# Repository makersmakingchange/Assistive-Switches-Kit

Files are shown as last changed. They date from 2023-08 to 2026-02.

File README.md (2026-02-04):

# Assistive Switches Kit
<!--- SUMMARY  --->

The [Assistive Switches Kit](https://www.makersmakingchange.com/s/product/assistive-switches-kit/01tJR0000006998YAA) provides an assortment of assistive switches and is intended to provide some different options if you want to try some devices, or get your AT Library started.

## Assistive Switches Kit
### Summary

| Name                 | MMC Library Link | GitHub Repository |                          
|----------------------|-----------------|---------------------------------------------------------------------------------------------------------------------------------------------|
| Raindrop Switch      | https://www.makersmakingchange.com/s/product/raindrop-switch/01tJR000000693tYAA | https://github.com/makersmakingchange/Raindrop-Switch |
| Light Touch Switch   | https://www.makersmakingchange.com/s/product/light-touch-switch/01tJR00000068zTYAQ | https://github.com/makersmakingchange/Light-Touch-Switch |
| Interact Switch      | https://www.makersmakingchange.com/s/product/interact-switch/01tJR000000698vYAA | https://github.com/makersmakingchange/Interact-Switch |
| MMC60 Switch         | https://makersmakingchange.com/s/product/mmc60-switch/01tJR000000693rYAA | https://github.com/makersmakingchange/MMC60_Assistive_Switch |

### Raindrop Switch
Low force switch well-suited for use by a finger or head.

### Light Touch Switch
Low force switch well-suited for use by a finger.

### Interact Switch
Medium force switch that is activated through applying pressure on the top surface.

### MMC60 Switch
The switch is activated by applying pressure on the top surface. This switch can be connected to any standard AT interface, and can also be used with the Xbox Adaptive Controller. The kit contains different colours and textures of interchangeable button tops.

---

<!-- ABOUT MMC START -->
## About Makers Making Change
[Makers Making Change Logo](https://www.makersmakingchange.com/)

Makers Making Change is a program of [Neil Squire](https://www.neilsquire.ca/), a Canadian non-profit that uses technology, knowledge, and passion to empower people with disabilities.

Makers Making Change leverages the capacity of community based Makers, Disability Professionals and Volunteers to develop and deliver affordable Open Source Assistive Technologies.

 - Website: [www.MakersMakingChange.com](https://www.makersmakingchange.com/)
 - GitHub: [makersmakingchange](https://github.com/makersmakingchange)
 - Bluesky: [@makersmakingchange.bsky.social](https://bsky.app/profile/makersmakingchange.bsky.social)
 - Instagram: [@makersmakingchange](https://www.instagram.com/makersmakingchange)
 - Facebook: [makersmakechange](https://www.facebook.com/makersmakechange)
 - LinkedIn: [Neil Squire Society](https://www.linkedin.com/company/neil-squire-society/)
 - Thingiverse: [makersmakingchange](https://www.thingiverse.com/makersmakingchange/about)
 - Printables: [MakersMakingChange](https://www.printables.com/@MakersMakingChange)

### Contact Us
For technical questions, to get involved, or to share your experience we encourage you to [visit our website](https://www.makersmakingchange.com/) or [contact us](https://www.makersmakingchange.com/s/contact).
<!-- ABOUT MMC END -->

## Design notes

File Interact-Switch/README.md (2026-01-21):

 # Interact Switch
<!---  SUMMARY A brief summary of the project. What it does, who it is for, how much it costs. --->

The Interact Switch is an open source assistive switch. The switch is comprised of 3D printed parts and off-the-shelf electronics. The Interact Switch is a high quality, modular 3D printable switch design. The tactile feel of the switch is on par with commercial switches, coming in at about 35 gf of activation force across the surface of the switch. The base has the same footprint as a Jellybean switch, and should work with any Jellybean switch mounts.

There are a wide array of different designs: from a simple flat button, to textured designs, to a dome, and even some wobble switch variants.

The switch base incorporates 6 slots that are ideal for a variety of mounting options, including using hook and loop straps (e.g., VELCRO). The overall cost of materials is about $8 (plus $8 for component shipping).

A 3D printed Interact Switch with smiley topper

## More info at
- [Makers Making Change Library Page](https://www.makersmakingchange.com/s/product/interact-switch/01tJR000000698vYAA)

## How to Obtain the Device
### 1. Do-it-Yourself (DIY) or Do-it-Together (DIT)

This is an open-source assistive technology, so anyone is free to build it. All of the files and instructions required to build the device are contained within this repository. Refer to the Maker Guide below.

### 2. Request a build of this device

You may also submit a build request through the [MMC Library Page](https://www.makersmakingchange.com/s/product/interact-switch/01tJR000000698vYAA) to have a volunteer maker build the device. As the requestor, you are responsible for reimbursing the maker for the cost of materials and any shipping.

### 3. Build this device for someone else

If you have the skills and equipment to build this device, and would like to donate your time to create the device for someone who needs it, visit the [MMC Maker Wanted](https://makersmakingchange.com/maker-wanted/) section.

## Build Instructions

### 1. Read through the Maker Guide

The Maker Guide  [EN](/Documentation/Interact_Switch_Maker_Guide.pdf), WIP <!---([FR](/Documentation/FR_Interact_Switch_Maker_Guide.pdf)) --->  contains all the necessary information to build this device, including tool lists, assembly instructions, programming instructions (if applicable) and testing.

### 2. Order the Off-The-Shelf Components

The [Bill of Materials](/Documentation/Interact_Switch_BOM.csv) lists all of the parts and components required to build the Interact Switch. The main switch component needs to be ordered online. The rest of the off-the-shelf components are also online or may be available in smaller quantities at your local hardware store or dollar store.

### 3. Print the 3D Printable components

All of the individual print files can be found in the [/Build_Files/3D_Printing_Files](/Build_Files/3D_Printing_Files/) folder.

### 4. Assemble the <Device-Name>

Reference the Assembly Guide([EN](/Documentation/Interact_Switch_Maker_Guide.pdf),[FR](/Documentation/FR_Interact_Switch_Assembly_Guide.pdf)) for the tools and steps required to build each portion.

## How to improve this Device
As open source assistive technology, you are welcomed and encouraged to improve upon the design. 

## Files
### Documentation
| Document             | Version | Link |
|----------------------|---------|------|
| Design Rationale     | 2.0     | [Interact_Switch_Design_Rationale](/Documentation/Interact_Switch_Design_Rationale.pdf)    |
| Maker Guide          | 2.0     | [Interact_Switch_Maker_Checklist](/Documentation/Interact_Switch_Maker_Guide.pdf)          |
| Topper Guide         | 2.0     | [Interact Switch Topper Guide](/Documentation/Interact_Switch_Topper_Guide.pdf)            |
| Bill of Materials    | 2.0     | [Interact_Switch_Bill_of_Materials](/Documentation/Interact_Switch_BOM.csv)                |
| User Guide           | 2.0     | [Interact_Switch_User_Guide](/Documentation/Interact_Switch_Quick_Guide.pdf)               |
| Changelog            | 2.0     | [Interact_Switch_Changelog](CHANGES.txt)     |

### Design Files
<!--- DESIGN FILES If possible, include a copy of original design files to facilitate easy editing and customization. --->
 - [CAD Files](/Design_Files/CAD_Design_Files)

### Build Files
 - [3D Printing Files](/Build_Files/3D_Printing_Files)

## Attribution
The [original design](https://github.com/mwturvey/InteractSwitch) of the Interact Switch was by Mike Turvey.

Modifications to the design and additional documentation by Neil Squire Society / Makers Making Change.
  - Increases the screw hole size in the ButtonCapHolder to accept #4 3/8" screws instead of M2.5 screws.
  - Lines up the holes in the base with the holes in the ButtonCapHolder.
  - Deepens the countersink in the Base for the screws.
  - Removes the need for supports on the Base piece.
  - Decreases the required sanding by tapering the tabs on the ButtonCapHolder.  

Because of the modifications made to the base and button cap holder to accomodate the #4 screws, they are no longer backwards compatible with the original files and is not longer compatible with M2.5 screws.

### Contributors
 - Mike Turvey
 - Stephen Moyer. Neil Squire Society.
 - Brad Wellington. Neil Squire Society.
 - Jake McIvor. Neil Squire Society.
---

<!-- ABOUT MMC START -->
## About Makers Making Change
[Makers Making Change Logo](https://www.makersmakingchange.com/)

Makers Making Change is a program of [Neil Squire](https://www.neilsquire.ca/), a Canadian non-profit that uses technology, knowledge, and passion to empower people with disabilities.

Makers Making Change leverages the capacity of community based Makers, Disability Professionals and Volunteers to develop and deliver affordable Open Source Assistive Technologies.

 - Website: [www.MakersMakingChange.com](https://www.makersmakingchange.com/)
 - GitHub: [makersmakingchange](https://github.com/makersmakingchange)
 - Bluesky: [@makersmakingchange.bsky.social](https://bsky.app/profile/makersmakingchange.bsky.social)
 - Instagram: [@makersmakingchange](https://www.instagram.com/makersmakingchange)
 - Facebook: [makersmakechange](https://www.facebook.com/makersmakechange)
 - LinkedIn: [Neil Squire Society](https://www.linkedin.com/company/neil-squire-society/)
 - Thingiverse: [makersmakingchange](https://www.thingiverse.com/makersmakingchange/about)
 - Printables: [MakersMakingChange](https://www.printables.com/@MakersMakingChange)

### Contact Us
For technical questions, to get involved, or to share your experience we encourage you to [visit our website](https://www.makersmakingchange.com/) or [contact us](https://www.makersmakingchange.com/s/contact).
<!-- ABOUT MMC END -->

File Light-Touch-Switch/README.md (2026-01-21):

<!--- Open Source Assistive Technology: GitHub Readme Template Version 1.2 (2024-May-27)  --->
<!--- TITLE --->
# Light Touch Switch
<!--- Should match the name of the GitHub repository. Choose something descriptive rather than whimsical.  --->

## Overview
<!--- A brief summary of the project. What it does, who it is for, how much it costs. --->
The Light Touch Switch is a low force, 3D printed assistive switch that works with standard switch adapted devices, like switch adapted toys; computer, phone, and tablet switch interfaces; and adapted gaming devices. 

The device is comprised of off-the-shelf electronics and 3D printed parts. 

The Light Touch Switch is open assistive technology (OpenAT). Under the terms of the open source licenses, the device may be built, used, and improved upon by anyone.

The overall cost of materials is about $5.90 CAD (plus $8 CAD for component shipping).

Picture of Light Touch Switch.

## Makers Making Change Assistive Device Library
- https://www.makersmakingchange.com/s/product/light-touch-switch/01tJR00000068zTYAQ

## How to Obtain the Device
### 1. Do-it-Yourself (DIY) or Do-it-Together (DIT)

This is an open-source assistive technology, so anyone is free to build it. All of the files and instructions required to build the device are contained within this repository. Refer to the Maker Guide below.

### 2. Request a build of this device

You may also submit a build request through the [Makers Making Change Assistive Device Library Listing](https://www.makersmakingchange.com/s/product/light-touch-switch/01tJR00000068zTYAQ) to have a volunteer maker build the device. As the requestor, you are responsible for reimbursing the maker for the cost of materials and any shipping.

### 3. Build this device for someone else

If you have the skills and equipment to build this device, and would like to donate your time to create the device for someone who needs it, visit the [MMC Maker Wanted](https://makersmakingchange.com/maker-wanted/) section.

## Build Instructions
<!--- Outline the major steps required to create a build --->

### 1. Read through the Maker Guide
The [Maker Guide](/Documentation/Light_Touch_Switch_Maker_Guide.pdf)  contains all the necessary information to build this device, including tool lists, assembly instructions, programming instructions (if applicable) and testing.

### 2. Order the Off-The-Shelf Components
The [Bill of Materials](/Documentation/Light_Touch_Switch_BOM.xlsx) lists all of the parts and components required to build the device.

### 3. Print the 3D Printable components
All of the files and individual print files can be found in the [/Build_Files/3D_Printing_Files](/Build_Files/3D_Printing_Files/) folder.

### 4. Assemble the Light Touch Switch
Reference the Assembly Guide section of the [Maker Guide](/Documentation/Light_Touch_Switch_Maker_Guide.pdf) for the tools and steps required to build the device.

## How to improve this Device
As open source assistive technology, you are welcomed and encouraged to improve upon the design. 

## Files
### Documentation
<!--- Update the name, link, and version for documentation --->
| Document             | Version | Link |
|----------------------|---------|------|
| Design Rationale     | 1.0     | [Light Touch Switch_Design_Rationale](/Documentation/Light_Touch_Switch_Design_Rationale.pdf)     |
| Maker Guide          | 1.0     | [Light Touch Switch_Maker_Checklist](/Documentation/Light_Touch_Switch_Maker_Guide.pdf)     |
| Bill of Materials    | 1.0     | [Light Touch Switch_Bill_of_Materials](/Documentation/Light_Touch_Switch_BOM.xlsx)     |
| User Guide           | 1.0     | [Light Touch Switch_User_Guide](/Documentation/Light_Touch_Switch_User_Guide.pdf)    |
| Changelog            | 1.0     | [Changelog](CHANGES.txt)     |

### Design Files
<!--- Include a copy of the original design files to facilitate easy editing and customization. Consider also including a generic format (e.g., STEP) --->
 - [CAD Files](/Design_Files/CAD_Design_Files)

### Build Files
<!--- Include a copy of the build files intended for manufacturing. This may include svg files for laser cutting, stl files for 3d printing, Gerber files for custom PCBs, and Arduino files for custom firmware. --->
 - [3D Printing Files](/Build_Files/3D_Printing_Files)

## License
<!--- Add the year(s) for the copyright and the Designer Name. You may use the standard set of open licenses or choose your own for the hardware, software, and accompanying materials. --->
Copyright (c) 2024 by Neil Squire.

This repository describes Open Hardware:
 - Everything needed or used to design, make, test, or prepare the Light Touch Switch is licensed under the [CERN 2.0 Weakly Reciprocal license (CERN-OHL-W v2) or later](https://cern.ch/cern-ohl ) .
 - All software is under the [GNU General Public License v3.0 (GPL-3.0)](https://www.gnu.org/licenses/gpl.html).
 - Accompanying material such as instruction manuals, videos, and other copyrightable works that are useful but not necessary to design, make, test, or prepare the <Device-Name> are published under a [Creative Commons Attribution-ShareAlike 4.0 license (CC BY-SA 4.0)](https://creativecommons.org/licenses/by-sa/4.0/) .

You may redistribute and modify this documentation and make products using it under the terms of the [CERN-OHL-W v2](https://cern.ch/cern-ohl).
This documentation is distributed WITHOUT ANY EXPRESS OR IMPLIED WARRANTY, INCLUDING OF MERCHANTABILITY, SATISFACTORY QUALITY AND FITNESS FOR A PARTICULAR PURPOSE.
Please see the CERN-OHL-W v2 for applicable conditions.

Source Location: https://github.com/makersmakingchange/Light-Touch-Switch

## Attribution
<!--- Provide any necessary attribution for designs or components that are included in the device or as part of the project. --->
 - The [original design](https://www.thingiverse.com/thing:3211154) was created by [Kevin Cross](https://www.thingiverse.com/davross/designs) and released with a [CC-BY license](https://creativecommons.org/licenses/by/4.0/). 
 - The design was modified and documentation was created by Neil Squire Society / Makers Making Change.
<!--- This is the attribution for the template. --->
 - The documentation template was created by Makers Making Change / Neil Squire Society and is used under a CC BY-SA 4.0 license. It is available at the following link: [https://github.com/makersmakingchange/OpenAT-Template](https://github.com/makersmakingchange/OpenAT-Template)

### Contributors
<!--- List the names of the people that contributed to the design. This could include the original source of the idea, designers, testers, documenters, etc. --->
Designers:
 - Neil Squire / Makers Making Change

----

<!-- ABOUT MMC START -->
## About Makers Making Change
[Makers Making Change Logo](https://www.makersmakingchange.com/)

Makers Making Change is a program of [Neil Squire](https://www.neilsquire.ca/), a Canadian non-profit that uses technology, knowledge, and passion to empower people with disabilities.

Makers Making Change leverages the capacity of community based Makers, Disability Professionals and Volunteers to develop and deliver affordable Open Source Assistive Technologies.

 - Website: [www.MakersMakingChange.com](https://www.makersmakingchange.com/)
 - GitHub: [makersmakingchange](https://github.com/makersmakingchange)
 - Bluesky: [@makersmakingchange.bsky.social](https://bsky.app/profile/makersmakingchange.bsky.social)
 - Instagram: [@makersmakingchange](https://www.instagram.com/makersmakingchange)
 - Facebook: [makersmakechange](https://www.facebook.com/makersmakechange)
 - LinkedIn: [Neil Squire Society](https://www.linkedin.com/company/neil-squire-society/)
 - Thingiverse: [makersmakingchange](https://www.thingiverse.com/makersmakingchange/about)
 - Printables: [MakersMakingChange](https://www.printables.com/@MakersMakingChange)

### Contact Us
For technical questions, to get involved, or to share your experience we encourage you to [visit our website](https://www.makersmakingchange.com/) or [contact us](https://www.makersmakingchange.com/s/contact).
<!-- ABOUT MMC END -->

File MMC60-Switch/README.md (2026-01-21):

<!-- Open Source Assistive Technology: GitHub Readme Template Version 1.1 (2024-Mar-15) -->

<!---
INSTRUCTIONS
This is a markdown template for creating the README.md file in a GitHub repository. This file is rendered and displayed automatically when someone visits the repository.

This document includes helper text that will not be displayed when rendered. Any text between the less-than sign + exclamation mark + three hyphen-minus (<!---) and matching three hyphen-minus + greater-than sign will not be displayed. This helper text can be deleted once the corresponding section is completed.

This template has a number of fields that can be searched and replaced with other text:
 - <Device_Name> Replace this with filename-friendly version of the device with underscores. e.g., Open_Wobble_Switch
 - <DeviceName> Replace this with the human-readable name of the device with spaces. e.g., Open Wobble Switch
 - <DesignerName> Replace this with the person or organization responsible for the design. e.g., John Doe.
 - <RepositoryLink> Replace this with the web address for the repository. e.g., (e.g., https://github.com/makersmakingchange/Open-Wobble-Switch))
 - <MMCWebLink> This is an alphanumeric id for the Makers Making Change Website. e.g., 01tJR000000698oYAA. This will come from MMC staff. 
 --->
 
 <!--- 
TITLE
Should match the name of the GitHub repository. Choose something descriptive rather than whimsical. 
 --->
# MMC60 Assistive Switch

2025-May-02: This repository is in the process of updating.

<!--- SUMMARY A brief summary of the project. What it does, who it is for, how much it costs.  --->
The <DeviceName> is an assistive technology widget that makes it easier to document Open-Source Assistive Technology devices. 

It is intended for use by makers. 

The device is comprised of off-the-shelf electronics and 3D printed parts. 

The overall cost of materials is about $<MaterialCost> (plus $<ShippingCost> for component shipping).

Picture of <DeviceName>.

## More info at
- [Makers Making Change Assistive Device Library Listing](<MMCWebLink>)

## How to Obtain the Device
### 1. Do-it-Yourself (DIY) or Do-it-Together (DIT)

This is an open-source assistive technology, so anyone is free to build it. All of the files and instructions required to build the device are contained within this repository. Refer to the Maker Guide below.

### 2. Request a build of this device

You may also submit a build request through the [Makers Making Change Assistive Device Library Listing](<MMCWebLink>) to have a volunteer maker build the device. As the requestor, you are responsible for reimbursing the maker for the cost of materials and any shipping.

### 3. Build this device for someone else

If you have the skills and equipment to build this device, and would like to donate your time to create the device for someone who needs it, visit the [MMC Maker Wanted](https://makersmakingchange.com/maker-wanted/) section.

## Build Instructions

### 1. Read through the Maker Guide

The [Maker Guide](/Documentation/<Device_Name>_Maker_Guide.pdf)  contains all the necessary information to build this device, including tool lists, assembly instructions, programming instructions (if applicable) and testing.

### 2. Order the Off-The-Shelf Components

The [Bill of Materials](/Documentation/<Device_Name>_BOM.xlsx) lists all of the parts and components required to build the device.

### 3. Print the 3D Printable components

All of the files and individual print files can be in the [/Build_Files/3D_Printing_Files](/Build_Files/3D_Printing_Files/) folder.

### 4. Assemble the <DeviceName>

Reference the [Assembly Guide](/Documentation/<Device_Name>_Assembly_Guide.pdf) for the tools and steps required to build each portion.

## How to improve this Device
As open source assistive technology, you are welcomed and encouraged to improve upon the design. 

## Files
### Documentation
| Document             | Version | Link |
|----------------------|---------|------|
| Design Rationale     | 1.0     | [<DeviceName>_Design_Rationale](/Documentation/<Device_Name>_Design_Rationale.pdf)     |
| Maker Guide          | 1.0     | [<DeviceName>_Maker_Checklist](/Documentation/<Device_Name>_Maker_Guide.pdf)     |
| Bill of Materials    | 1.0     | [<DeviceName>_Bill_of_Materials](/Documentation/<Device_Name>_BOM.xlsx)     |
| User Guide           | 1.0     | [<DeviceName>_User_Guide](/Documentation/<Device_Name>_Quick_Guide.pdf)    |
| Changelog            | 1.0     | [Changelog](CHANGES.txt)     |

### Design Files
<!---
DESIGN FILES
Include a copy of the original design files to facilitate easy editing and customization. Consider also including a generic format (e.g., STEP)
--->
 - [CAD Files](/Design_Files/CAD_Design_Files)
 - [PCB Files](/Design_Files/PCB_Design_Files)

<!---
BUILD FILES
Include a copy of the build files intended for manufacturing. This may include svg files for laser cutting, stl files for 3d printing, Gerber files for custom PCBs, and Arduino files for custom firmware
--->
### Build Files
 - [3D Printing Files](/Build_Files/3D_Printing_Files)
 - [PCB Build Files](/Build_Files/PCB_Build_Files)
 - [Firmware Files](/Build/Firmware_Files)

<!---
ATTRIBUTION
Provide any necessary attribution for designs or components that are included in the device or as part of the project.
--->
## Attribution

The device was designed by <DesignerName>. 

<!---
This is the attribution for the template.
--->
The documentation template was created by Makers Making Change / Neil Squire Society and is used under a CC BY-SA 4.0 license. It is available at the following link: [https://github.com/makersmakingchange/OpenAT-Template](https://github.com/makersmakingchange/OpenAT-Template)

<!---
CONTRIBUTORS
List the names of the people that contributed to the design. This could include the original source of the idea, designers, testers, documenters, etc.
--->
### Contributors

Designers:
 - Designer 1 
 - Designer 2

<!---
LICENSE
Add the year(s) for the copyright and the Designer Name. You may use the standard set of open licenses or choose your own for the hardware, software, and accompanying materials.
--->
## License
Copyright (c) YYYY <DesignerName>.

This repository describes Open Hardware:
 - Everything needed or used to design, make, test, or prepare the <Device-Name> is licensed under the [CERN 2.0 Weakly Reciprocal license (CERN-OHL-W v2) or later](https://cern.ch/cern-ohl ) .
 - All software is under the [GNU General Public License v3.0 (GPL-3.0)](https://www.gnu.org/licenses/gpl.html).
 - Accompanying material such as instruction manuals, videos, and other copyrightable works that are useful but not necessary to design, make, test, or prepare the <Device-Name> are published under a [Creative Commons Attribution-ShareAlike 4.0 license (CC BY-SA 4.0)](https://creativecommons.org/licenses/by-sa/4.0/) .

You may redistribute and modify this documentation and make products using it under the terms of the [CERN-OHL-W v2](https://cern.ch/cern-ohl).
This documentation is distributed WITHOUT ANY EXPRESS OR IMPLIED WARRANTY, INCLUDING OF MERCHANTABILITY, SATISFACTORY QUALITY AND FITNESS FOR A PARTICULAR PURPOSE.
Please see the CERN-OHL-W v2 for applicable conditions.

Source Location: <Repository_Link> 

---

<!-- ABOUT MMC START -->
## About Makers Making Change
[Makers Making Change Logo](https://www.makersmakingchange.com/)

Makers Making Change is a program of [Neil Squire](https://www.neilsquire.ca/), a Canadian non-profit that uses technology, knowledge, and passion to empower people with disabilities.

Makers Making Change leverages the capacity of community based Makers, Disability Professionals and Volunteers to develop and deliver affordable Open Source Assistive Technologies.

 - Website: [www.MakersMakingChange.com](https://www.makersmakingchange.com/)
 - GitHub: [makersmakingchange](https://github.com/makersmakingchange)
 - Bluesky: [@makersmakingchange.bsky.social](https://bsky.app/profile/makersmakingchange.bsky.social)
 - Instagram: [@makersmakingchange](https://www.instagram.com/makersmakingchange)
 - Facebook: [makersmakechange](https://www.facebook.com/makersmakechange)
 - LinkedIn: [Neil Squire Society](https://www.linkedin.com/company/neil-squire-society/)
 - Thingiverse: [makersmakingchange](https://www.thingiverse.com/makersmakingchange/about)
 - Printables: [MakersMakingChange](https://www.printables.com/@MakersMakingChange)

### Contact Us
For technical questions, to get involved, or to share your experience we encourage you to [visit our website](https://www.makersmakingchange.com/) or [contact us](https://www.makersmakingchange.com/s/contact).
<!-- ABOUT MMC END -->

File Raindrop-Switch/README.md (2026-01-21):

<!--- TITLE --->
# Raindrop Switch
<!--- Should match the name of the GitHub repository. Choose something descriptive rather than whimsical.  --->

## Overview
<!--- A brief summary of the project. What it does, who it is for, how much it costs. --->
The Raindrop Switch is an assistive technology device that works with standard switch adapted devices, like switch adapted toys; computer, phone, and tablet switch interfaces; and adapted gaming devices. . 

The device is comprised of off-the-shelf electronics and 3D printed parts. 

The Raindrop Switch is open assistive technology (OpenAT). Under the terms of the open source licenses, the device may be built, used, and improved upon by anyone.

The overall cost of materials is about $3.53 CAD (plus $8 CAD for component shipping).

Picture of Raindrop Switch.

## Makers Making Change Assistive Device Library
- https://www.makersmakingchange.com/s/product/raindrop-switch/01tJR000000693tYAA

## How to Obtain the Device
### 1. Do-it-Yourself (DIY) or Do-it-Together (DIT)

This is an open-source assistive technology, so anyone is free to build it. All of the files and instructions required to build the device are contained within this repository. Refer to the Maker Guide below.

### 2. Request a build of this device

You may also submit a build request through the [Makers Making Change Assistive Device Library Listing](https://www.makersmakingchange.com/s/product/raindrop-switch/01tJR000000693tYAA) to have a volunteer maker build the device. As the requestor, you are responsible for reimbursing the maker for the cost of materials and any shipping.

### 3. Build this device for someone else

If you have the skills and equipment to build this device, and would like to donate your time to create the device for someone who needs it, visit the [MMC Maker Wanted](https://makersmakingchange.com/maker-wanted/) section.

## Build Instructions
<!--- Outline the major steps required to create a build --->

### 1. Read through the Maker Guide

The [Maker Guide](/Documentation/Raindrop_Switch_Maker_Guide.pdf)  contains all the necessary information to build this device, including tool lists, assembly instructions, programming instructions (if applicable) and testing.

### 2. Order the Off-The-Shelf Components

The [Bill of Materials](/Documentation/Raindrop_Switch_BOM.xlsx) lists all of the parts and components required to build the device.

### 3. Print the 3D Printable components

All of the files and individual print files can be found in the [/Build_Files/3D_Printing_Files](/Build_Files/3D_Printing_Files/) folder.

### 4. Assemble the Raindrop Switch

Reference the Assembly Guide section of the [Maker Guide](/Documentation/Raindrop_Switch_Maker_Guide.pdf) for the tools and steps required to build the device.

## How to improve this Device
As open source assistive technology, you are welcomed and encouraged to improve upon the design. 

## Files
### Documentation
<!--- Update the name, link, and version for documentation --->
| Document             | Version | Link |
|----------------------|---------|------|
| Design Rationale     | 1.1     | [Raindrop_Switch_Design_Rationale](/Documentation/Raindrop_Switch_Design_Rationale.pdf)     |
| Maker Guide          | 1.1     | [Raindrop_Switch_Maker_Checklist](/Documentation/Raindrop_Switch_Maker_Guide.pdf)     |
| Bill of Materials    | 1.1     | [Raindrop Switch_Bill_of_Materials](/Documentation/Raindrop_Switch_BOM.xlsx)     |
| User Guide           | 1.1     | [Raindrop Switch_User_Guide](/Documentation/Raindrop_Switch_User_Guide.pdf)    |
| Changelog            | 1.1     | [Changelog](CHANGES.txt)     |

### Design Files
<!--- Include a copy of the original design files to facilitate easy editing and customization. Consider also including a generic format (e.g., STEP) --->
 - [CAD Files](/Design_Files/CAD_Design_Files)

### Build Files
<!--- Include a copy of the build files intended for manufacturing. This may include svg files for laser cutting, stl files for 3d printing, Gerber files for custom PCBs, and Arduino files for custom firmware. --->
 - [3D Printing Files](/Build_Files/3D_Printing_Files)

## License
<!--- Add the year(s) for the copyright and the Designer Name. You may use the standard set of open licenses or choose your own for the hardware, software, and accompanying materials. --->
Copyright (c) 2024 Neil Squire.

This repository describes Open Hardware:
 - Everything needed or used to design, make, test, or prepare the Raindrop Switch is licensed under the [CERN 2.0 Weakly Reciprocal license (CERN-OHL-W v2) or later](https://cern.ch/cern-ohl ) .
 - All software is under the [GNU General Public License v3.0 (GPL-3.0)](https://www.gnu.org/licenses/gpl.html).
 - Accompanying material such as instruction manuals, videos, and other copyrightable works that are useful but not necessary to design, make, test, or prepare the <Device-Name> are published under a [Creative Commons Attribution-ShareAlike 4.0 license (CC BY-SA 4.0)](https://creativecommons.org/licenses/by-sa/4.0/) .

You may redistribute and modify this documentation and make products using it under the terms of the [CERN-OHL-W v2](https://cern.ch/cern-ohl).
This documentation is distributed WITHOUT ANY EXPRESS OR IMPLIED WARRANTY, INCLUDING OF MERCHANTABILITY, SATISFACTORY QUALITY AND FITNESS FOR A PARTICULAR PURPOSE.
Please see the CERN-OHL-W v2 for applicable conditions.

Source Location: https://github.com/makersmakingchange/Raindrop-Switch

## Attribution
<!--- Provide any necessary attribution for designs or components that are included in the device or as part of the project. --->
The device was designed by Neil Squire. 

<!--- This is the attribution for the template. --->
The documentation template was created by Makers Making Change / Neil Squire Society and is used under a CC BY-SA 4.0 license. It is available at the following link: [https://github.com/makersmakingchange/OpenAT-Template](https://github.com/makersmakingchange/OpenAT-Template)

### Contributors
<!--- List the names of the people that contributed to the design. This could include the original source of the idea, designers, testers, documenters, etc. --->
 Jake McIvor

---

<!-- ABOUT MMC START -->
## About Makers Making Change
[Makers Making Change Logo](https://www.makersmakingchange.com/)

Makers Making Change is a program of [Neil Squire](https://www.neilsquire.ca/), a Canadian non-profit that uses technology, knowledge, and passion to empower people with disabilities.

Makers Making Change leverages the capacity of community based Makers, Disability Professionals and Volunteers to develop and deliver affordable Open Source Assistive Technologies.

 - Website: [www.MakersMakingChange.com](https://www.makersmakingchange.com/)
 - GitHub: [makersmakingchange](https://github.com/makersmakingchange)
 - Bluesky: [@makersmakingchange.bsky.social](https://bsky.app/profile/makersmakingchange.bsky.social)
 - Instagram: [@makersmakingchange](https://www.instagram.com/makersmakingchange)
 - Facebook: [makersmakechange](https://www.facebook.com/makersmakechange)
 - LinkedIn: [Neil Squire Society](https://www.linkedin.com/company/neil-squire-society/)
 - Thingiverse: [makersmakingchange](https://www.thingiverse.com/makersmakingchange/about)
 - Printables: [MakersMakingChange](https://www.printables.com/@MakersMakingChange)

### Contact Us
For technical questions, to get involved, or to share your experience we encourage you to [visit our website](https://www.makersmakingchange.com/) or [contact us](https://www.makersmakingchange.com/s/contact).
<!-- ABOUT MMC START -->
## About Makers Making Change
[Makers Making Change Logo](https://www.makersmakingchange.com/)

Makers Making Change is a program of [Neil Squire](https://www.neilsquire.ca/), a Canadian non-profit that uses technology, knowledge, and passion to empower people with disabilities.

Makers Making Change leverages the capacity of community based Makers, Disability Professionals and Volunteers to develop and deliver affordable Open Source Assistive Technologies.

 - Website: [www.MakersMakingChange.com](https://www.makersmakingchange.com/)
 - GitHub: [makersmakingchange](https://github.com/makersmakingchange)
 - Bluesky: [@makersmakingchange.bsky.social](https://bsky.app/profile/makersmakingchange.bsky.social)
 - Instagram: [@makersmakingchange](https://www.instagram.com/makersmakingchange)
 - Facebook: [makersmakechange](https://www.facebook.com/makersmakechange)
 - LinkedIn: [Neil Squire Society](https://www.linkedin.com/company/neil-squire-society/)
 - Thingiverse: [makersmakingchange](https://www.thingiverse.com/makersmakingchange/about)
 - Printables: [MakersMakingChange](https://www.printables.com/@MakersMakingChange)

### Contact Us
For technical questions, to get involved, or to share your experience we encourage you to [visit our website](https://www.makersmakingchange.com/) or [contact us](https://www.makersmakingchange.com/s/contact).

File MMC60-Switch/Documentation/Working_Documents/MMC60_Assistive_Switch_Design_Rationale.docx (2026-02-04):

# Introduction

The MMC60 is an assistive switch with a 60 mm diameter top. It is meant to be a robust switch with an integrated ¼-20 mounting option for users who require a large, robust switch.

This Design Rationale is a work in progress, and has been saved as a PDF for use with some automated device repository updates.

# Research

<Existing Commercial Options>

Title
Link
Author
License
Cost
Notes

<DIY designs>

Title
Link
Author
License
Cost
Test Build (Y/N)
Add to Library (Y/N)
Notes

# Requirements

## Goals

G01
G02
G03

## Functional Requirements

F01
F02
F03

## Non-functional Requirement

NF01
NF02
NF03

## Constraints

C01
C02
C03

# Ideation

# Conceptual Design

## Concept 1

## Concept 2

## Concept 3

# Prototyping

# Testing

# Detailed Design

# Opportunities for Improvement

© 2023 by <Author>. This work is licensed under the CC BY SA 4.0 License: http://creativecommons.org/licenses/by-sa/4.0 Files available at <Replace with MMC Library Link> Page 1 of 1

V1.0 | Feb 2026 MMC60 Assistive Switch Design Rationale

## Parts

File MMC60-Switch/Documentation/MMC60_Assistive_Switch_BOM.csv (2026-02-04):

Device: MMC60_Assistive_Switch |  | Total Cost | Total Print time (hr) | Total filament (g)
Version: V1.0 | Date Created: Feb 2, 2026 | $12.14 | 1.97 | 39.4
Commercial Parts:
Part type (Electrical. Mechanical, Sanitization, ect) | Part Name | Quantity Needed | Pkg Quantity | Price per package | Price per Unit | Price for qty needed | Link
 | 3.5mm Mono Jack | 1 | 1 | $2.47 | $2.47 | $2.47 | https://www.digikey.ca/en/products/detail/cui-inc/MJ-3502/281321
 | #4 3/8 length screw | 5 | 1 | $0.52 | $0.52 | $2.59 | https://www.digikey.ca/en/products/detail/serpac/6005/307599
 | 1/4-20 Hex nut | 2 | 1 | $0.22 | $0.22 | $0.44 | https://www.digikey.ca/en/products/detail/80-20-llc/24202/28311218
 | 1/4-20, 1/2" length Hex Bolt | 1 | 1 | $0.58 | $0.58 | $0.58 | https://www.homedepot.ca/product/paulin-1-4-20-x-1-2-inch-hex-head-cap-screw-18-8-stainless-steel-unc/1000142251
 | 1/4-20, 5/16" length T-Nut | 1 | 1 | $0.55 | $0.55 | $0.55 | https://www.homedepot.ca/product/paulin-1-4-inch-20-tee-nuts-4-prong-5-16-inch-barrel-length/1000129429
 | 3.5 mm Mono Cable, 10 ft, Male to Male | 1 | 1 | 2.89 | $2.89 | $2.89 | https://www.primecables.ca/p-370665-cab-aud-200-all-35mm-18-inch-mono-ts-male-to-male-28awg-ft4-cable-black
 | Limit Switch | 1 | 1 | 1.55 | $1.55 | $1.55 | https://www.digikey.ca/en/products/detail/omron-electronics-inc-emc-div/SS-3GP/664724
3D Printed Parts ESTIMATED PRICING USING 1KG ROLL COST: | $25.00
Part | Description | Quantity Needed | TOTAL Mass (g) | Estimated Price | Print Time (Min) | Link
MMC60_Base_Bottom_EN-FR |  | 1 | 20.74 | $0.52 | 56
MMC60_Button |  | 1 | 9.2 | $0.23 | 24
RFS_Base_Top |  | 1 | 5.67 | $0.14 | 16
RFS_Flexure |  | 1 | 3.53 | $0.09 | 15
RFS_Pins |  | 1 | 0.26 | $0.01 | 7
RFS_Sw_Jack_Mount |  | 1 | 3.54 | $0.09 | 15
 |  |  | Total Print Cost: | $1.07
Tools for Assembly
Alternatives (if there are other sources for some parts link them below)
Part and description | Link
#4 3/8 length screw | https://a.co/d/0fvi6Sdn
1/4-20 Hex nut | https://a.co/d/04irVJAz
1/4-20, 1/2" length Hex Bolt | https://a.co/d/0aEeQ1J0
1/4-20, 5/16" length T-Nut | https://a.co/d/083bJTZo

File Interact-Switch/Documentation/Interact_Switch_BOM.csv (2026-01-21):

Device: | Interact Switch
Version: | V2.0
Last Updated: | 2025-07-08
 |  |  |  |  |  |  |  | Total filament (g) |  | Unit Cost | Total Estimated Cost | Build Cost
 |  |  |  |  |  |  |  | 35 |  | $8.70 | $8.70
ID | Commercial Parts |  |  |  |  |  |  |  |  | $7.82 | $7.82
 | Part | Description |  | Manufacturer | Supplier | QTY / Device | QTY / PKG | PKGs | $/ PKG | $ / Device | Total Estimated Cost |  | Link
 | Mono Cable |  |  |  | Digikey | 1 | 1 | 1 | $4.65 | $4.65 | $4.65 |  | https://www.digikey.ca/en/products/detail/tensility-international-corp/10-00344/2350247
 | Snap Action Switch |  |  |  | Digikey | 1 | 1 | 1 | $1.40 | $1.40 | $1.40 |  | https://www.digikey.ca/en/products/detail/omron-electronics-inc-emc-div/SS-3GP/664724
 | #4 Sheet Metal Screw |  |  |  | Digikey | 3 | 1 | 3 | $0.59 | $1.77 | $1.77 |  | https://www.digikey.ca/en/products/detail/serpac/6005/307599
 |  |  |  |  |  |  |  | 0 |  | $- | $-
 |  |  |  |  |  |  |  | 0 |  | $- | $-
 | 3D Printed Parts |  |  |  |  |  |  | 35 |  | $0.88 | $0.88
 | Part | Description | Filament Type | Filament | Color | QTY / Device | Mass (g) / Part | Total Mass | $ / kg | $ / Device | Total Estimated Cost |  | Link
 | Interact_Switch_Base |  | PLA |  | Any | 1 | 17 | 17 | $25.00 | $0.43 | $0.43
 | Interact_Switch_Cap_Plain |  | PLA |  | Any | 1 | 14 | 14 | $25.00 | $0.35 | $0.35
 | Interact_Switch_Holder |  | PLA |  | Any | 1 | 3 | 3 | $25.00 | $0.08 | $0.08
 | Interact_Switch_Insert_0.6mm |  | PLA |  | Any | 1 | 1 | 1 | $25.00 | $0.03 | $0.03
 |  |  |  |  |  |  |  | 0 |  | $- | $-
 |  |  |  |  |  |  |  | 0 |  | $- | $-
 |  |  |  |  |  |  |  | 0 |  | $- | $-
 |  |  |  |  |  |  |  | 0 |  | $- | $-

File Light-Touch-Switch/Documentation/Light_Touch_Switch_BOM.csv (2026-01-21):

Device: | Light Touch Switch
Version: | V1.0.0
Last Updated: | 2024-06-26
 |  |  |  |  |  |  |  | Total filament (g) |  | Unit Cost | Total Estimated Cost | Build Cost
 |  |  |  |  |  |  |  | 8 |  | $5.89 | $5.89
Maker Guide ID | Commercial Parts |  |  |  |  |  |  |  |  | $5.69 | $5.69
 | Part | Description |  | Manufacturer | Supplier | QTY / Device | QTY / PKG | PKGs | $/ PKG | $ / Device | Total Estimated Cost |  | Link
A01 | Tactile switch | Tactile switch for controlling devices |  | Omron | Digikey | 1 | 1 | 1 | $1.02 | $1.02 | $1.02 |  | https://www.digikey.ca/en/products/detail/omron-electronics-inc-emc-div/B3F-5050/368377?s=N4IgTCBcDaIEIGYBiBaArABkyAugXyA
A02 | 3.5 mm mono cable (6 foot length) | Cable to connect to an assistive device |  | Tensility International Corp | Digikey | 1 | 1 | 1 | $4.67 | $4.67 | $4.67 |  | https://www.digikey.ca/en/products/detail/tensility-international-corp/10-00344/2350247
 |  |  |  |  |  |  |  | 0 |  | $- | $-
 |  |  |  |  |  |  |  | 0 |  | $- | $-
 |  |  |  |  |  |  |  | 0 |  | $- | $-
 | 3D Printed Parts |  |  |  |  |  |  | 12 |  | $0.20 | $0.20
 | Part | Description | Filament Type | Filament | Color | QTY / Device | Mass (g) / Part | Total Mass | $ / kg | $ / Device | Total Estimated Cost |  | Link
A03 | LTS_Base_v1.0.stl | Switch base | PLA |  | Any | 1 | 3 | 3 | $25.00 | $0.08 | $0.08
A04 | LTS_Cap_v1.0.stl | Switch top | PLA |  | Any | 1 | 4 | 4 | $25.00 | $0.10 | $0.10
A05 | LTS_Pin_v0.1.stl | Pins for holding base and top together | PLA |  | Any | 1 | 1 | 1 | $25.00 | $0.03 | $0.03
T06 | Switch_Jig_12mm_V1.0.stl | Optional 3D printed jig to hold tactile switch while soldering | PLA |  | Any | 1 | 4 | 4
 | Tools
 | Tool | Description |  | Manufacturer | Supplier |  |  |  |  |  |  |  | Link
T01 | Wire cutter / stripper
T02 | Flush cutter
T03 | Soldering iron
T04 | Hot glue gun
T05 | Needle Nosed Pliers
T07 | Switch Testing Device
 | Alternatives
 | Part | Description |  | Manufacturer | Supplier | QTY / Device | QTY / PKG | PKGs | $/ PKG | $ / Device | Total Estimated Cost |  | Link
A01 | Tactile switch | Tactile switch for controlling devices |  | Omron | Mouser | 1 | 1 | 1 | $0.83 | $0.83 | $0.83 |  | https://www.mouser.ca/ProductDetail/Omron-Electronics/B3F-5050?qs=dOLq8QE0Pqqk%2FO9x2OpTQw%3D%3D
A02 | 3.5mm mono cable (six foot length) | Cable to connect to assistive devices |  | My Cable Mart | My Cable Mart | 0.5 | 1 | 1 | $1.77 | $0.89 | $1.77 |  | https://www.mycablemart.com/store/cart.php?m=product_detail&p=5537
A02 | 3.5mm mono cable (six foot length) | Cable to connect to assistive devices |  | Prime Cables | Prime Cable | 0.5 | 1 | 1 | 2.29 | 1.145 | 2.29 |  | https://www.primecables.ca/p-370665-cab-aud-200-all-35mm-18-inch-mono-ts-male-to-male-28awg-ft4-cable-black?from_pla=google&sku=383505&gad_source=1
A02 | 3.5 mm stereo cable (6 foot length) | Cable to connect to assistive devices. Note: You will need to do extra work to ensure the tip, ring, and sleeve are connected properly. |  | Prime Cables | Prime Cables | 0.5 | 1 | 1 | $1.99 | $1.00 | $1.99 |  | https://www.primecables.ca/p-391548-cab-aud-220-06-6ft-35mm-stereo-male-to-male-cable-riser-rated-cl2ft4-black?from_pla=google&sku=417835&gad_source=1

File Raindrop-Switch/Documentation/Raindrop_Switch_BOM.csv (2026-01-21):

Device: | Raindrop Switch
Version: | V1.1
Last Updated: | 2024-06-25
 |  |  |  |  |  |  |  | Total filament (g) |  | Unit Cost | Total Estimated Cost | Build Cost
 |  |  |  |  |  |  |  | 6 |  | $3.53 | $6.01
ID | Commercial Parts |  |  |  |  |  |  |  |  | $3.38 | $5.86
 | Part | Description |  | Manufacturer | Supplier | QTY / Device | QTY / PKG | PKGs | $/ PKG | $ / Device | Total Estimated Cost |  | Link
A01 | Press Button | Tactile button |  | Omron Electronics | Digikey | 1 | 1 | 1 | $1.04 | $1.04 | $1.04 |  | https://www.digikey.ca/en/products/detail/omron-electronics-inc-emc-div/B3F-5050/368377
A02 | Mono Cable | 3.5mm mono cable |  | Tensility International Corp | Digikey | 1 | 2 | 1 | $4.67 | $2.34 | $4.67 |  | https://www.digikey.ca/en/products/detail/tensility-international-corp/10-00344/2350247
 |  |  |  |  |  |  |  | 0 | $- | $- | $-
 |  |  |  |  |  |  |  | 0 | $- | $- | $-
 |  |  |  |  |  |  |  | 0 | $- | $- | $-
 | 3D Printed Parts |  |  |  |  |  |  | 6 |  | $0.15 | $0.15
 | Part | Description | Filament Type | Filament | Color | QTY / Device | Mass (g) / Part | Total Mass | $ / kg | $ / Device | Total Estimated Cost |  | Link
A03 | Raindrop_Base_v1.2 | Base of the switch | PLA |  | Any | 1 | 1 | 1 | $25.00 | $0.03 | $0.03
A04 | Raindrop_Cap_v1.0 | Cap of the switch | PLA |  | Any | 1 | 1 | 1 | $25.00 | $0.03 | $0.03
T06 | Switch_Jig_12mm_v1.0 | Jig used to help solder to the button | PLA |  | Any | 1 | 4 | 4 | $25.00 | $0.10 | $0.10
 |  |  |  |  |  |  |  | 0 |  | $- | $-
 |  |  |  |  |  |  |  | 0 |  | $- | $-
 | Tools
 | Tool | Description |  | Manufacturer | Supplier |  |  |  |  |  |  |  | Link
T01 | Flush Cutters
T02 | Soldering Iron
T03 | Hot Glue Gun
T04 | Pliers
T05 | Wire Strippers
 | Alternatives
 | Part | Description |  | Manufacturer | Supplier | QTY / Device | QTY / PKG | PKGs | $/ PKG | $ / Device | Total Estimated Cost |  | Link
A01 | Press button | Tactile switch for controlling devices |  | Omron | Mouser | 1 | 1 | 1 | $0.83 | $0.83 | $0.83 |  | https://www.mouser.ca/ProductDetail/Omron-Electronics/B3F-5050?qs=dOLq8QE0Pqqk%2FO9x2OpTQw%3D%3D
A02 | Mono Cable | Cable to connect to assistive devices |  | My Cable Mart | My Cable Mart | 0.5 | 1 | 1 | $1.77 | $0.89 | $1.77 |  | https://www.mycablemart.com/store/cart.php?m=product_detail&p=5537
 | 3.5 mm stereo cable (6 foot length) | Cable to connect to assistive devices. Note: You will need to do extra work to ensure the tip, ring, and sleeve are connected properly. |  | Prime Cables | Prime Cables | 0.5 | 1 | 1 | $1.99 | $1.00 | $1.99 |  | https://www.primecables.ca/p-391548-cab-aud-220-06-6ft-35mm-stereo-male-to-male-cable-riser-rated-cl2ft4-black?from_pla=google&sku=417835&gad_source=1

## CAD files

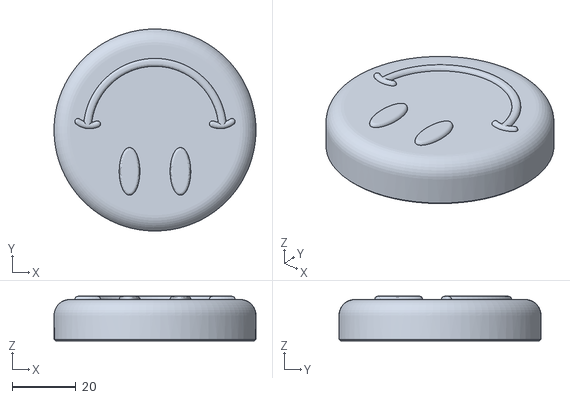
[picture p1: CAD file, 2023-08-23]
Interact-Switch/Build_Files/3D_Printing_Files/Alternate_Caps/ButtonCap_Smile.STL
63.5 x 63.5 x 14.0

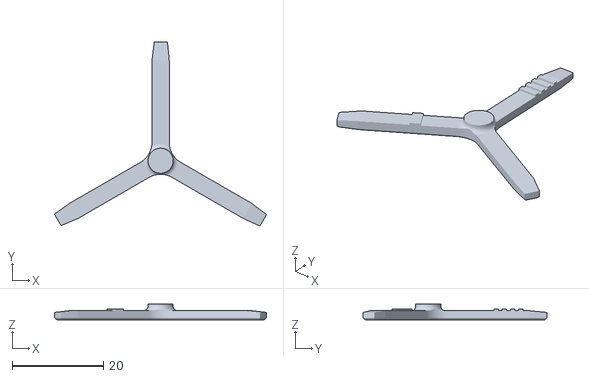
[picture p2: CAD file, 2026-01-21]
Interact-Switch/Build_Files/3D_Printing_Files/Alternate_Inserts/ButtonCapInsert_1.4mm.STL
46.4 x 40.3 x 3.40

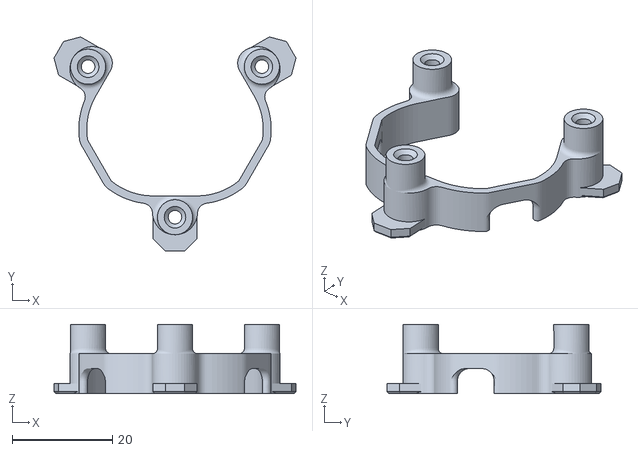
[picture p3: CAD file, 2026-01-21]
Interact-Switch/Build_Files/3D_Printing_Files/Interact_Switch_Holder.stl
48.2 x 42.7 x 13.9

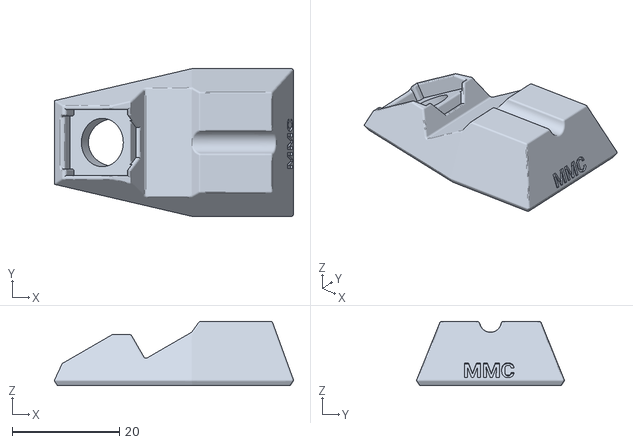
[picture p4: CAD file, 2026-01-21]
Light-Touch-Switch/Build_Files/3D_Printing_Files/Switch_Jig_12mm_V1.0.stl
44.5 x 27.5 x 11.9

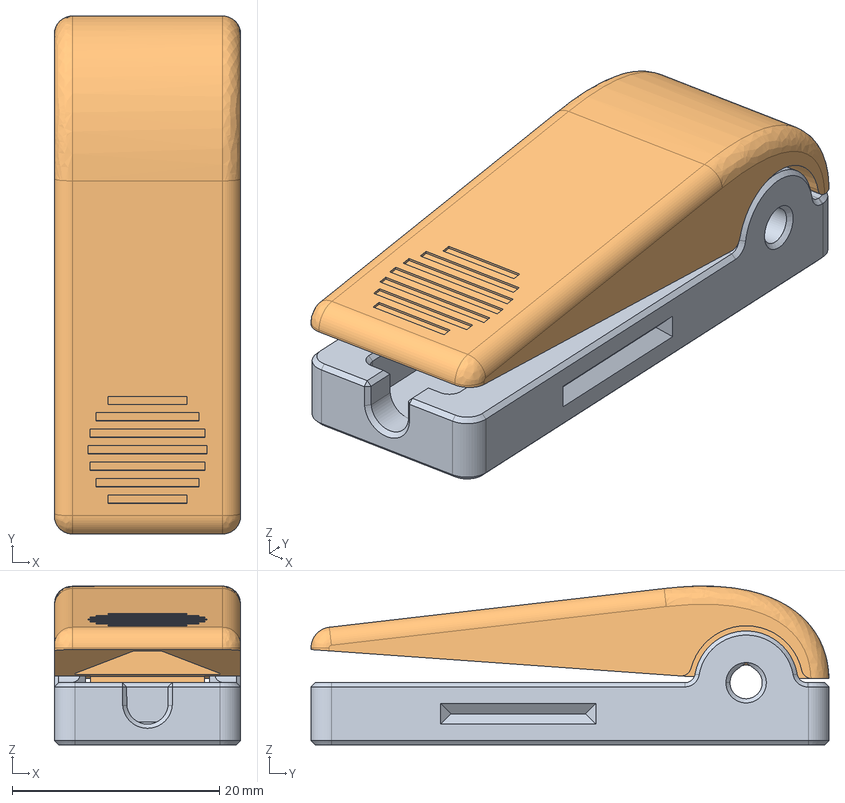
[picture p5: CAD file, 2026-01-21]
Light-Touch-Switch/Design_Files/CAD_Design_Files/Step/LTS_v1.step
18.0 x 50.0 x 15.3 mm
Base
Cap
Tactile Switch
Cable
Hole Sizing Jig

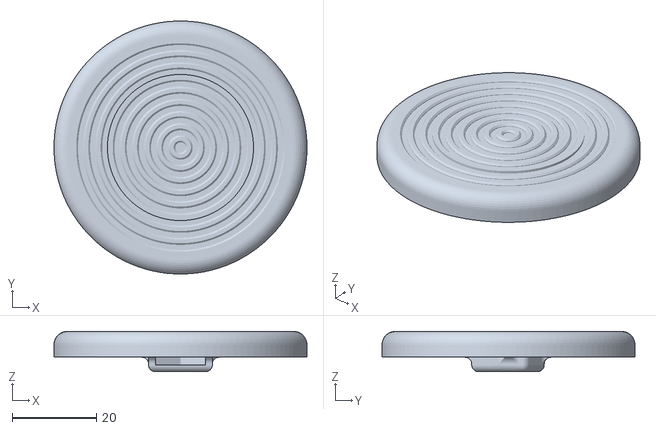
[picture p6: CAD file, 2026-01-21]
MMC60-Switch/Build_Files/3D_Printing_Files/Custom_Tops/MMC60_Button_Rings2.stl
60.0 x 60.0 x 9.56

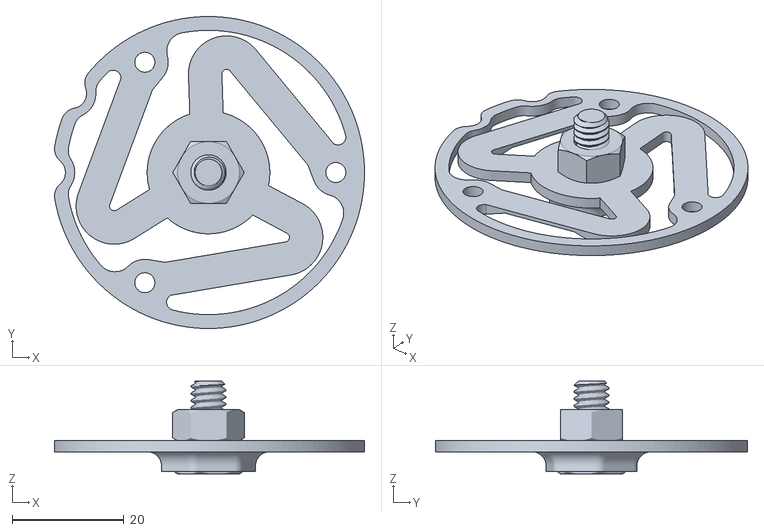
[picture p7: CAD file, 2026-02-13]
MMC60-Switch/Build_Files/3D_Printing_Files/RFS_Flexure.stl
55.6 x 56.0 x 16.7

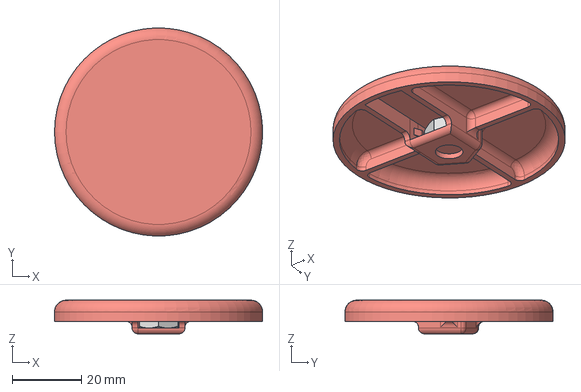
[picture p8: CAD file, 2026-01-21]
MMC60-Switch/Design_Files/CAD_Design_Files/MMC60_Switch_Button.step
60.0 x 60.0 x 9.70 mm

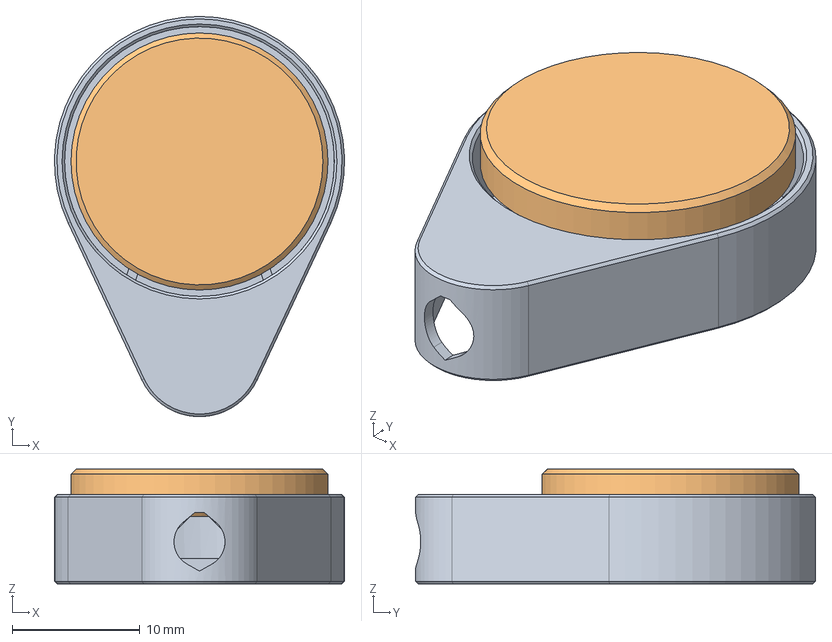
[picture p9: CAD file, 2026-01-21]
Raindrop-Switch/Design_Files/Raindrop_V1.2.step
22.7 x 31.4 x 9.00 mm
Base
Cap

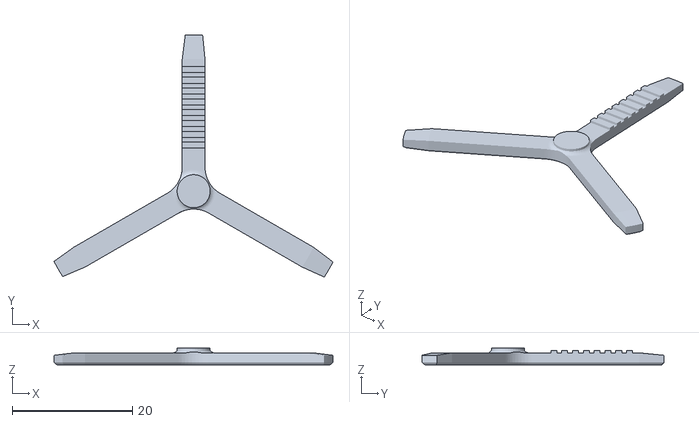
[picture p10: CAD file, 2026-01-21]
Interact-Switch/Build_Files/3D_Printing_Files/Alternate_Inserts/ButtonCapInsert_0.8mm.STL
46.4 x 40.3 x 2.80

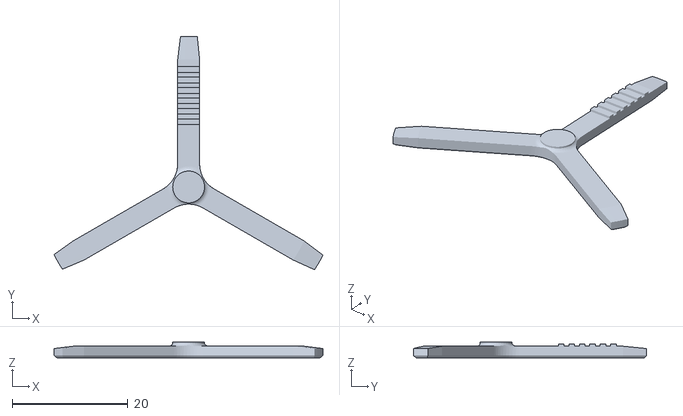
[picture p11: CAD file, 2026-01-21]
Interact-Switch/Build_Files/3D_Printing_Files/Interact_Switch_Insert_0.6mm.stl
46.4 x 40.3 x 2.70

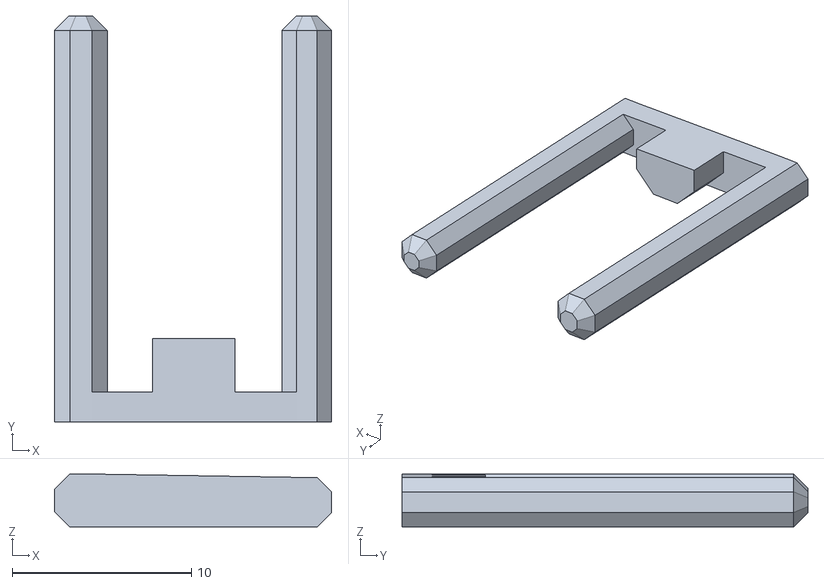
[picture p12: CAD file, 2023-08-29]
Light-Touch-Switch/Build_Files/3D_Printing_Files/LTS_Pin_v0.1.stl
15.5 x 22.7 x 2.96

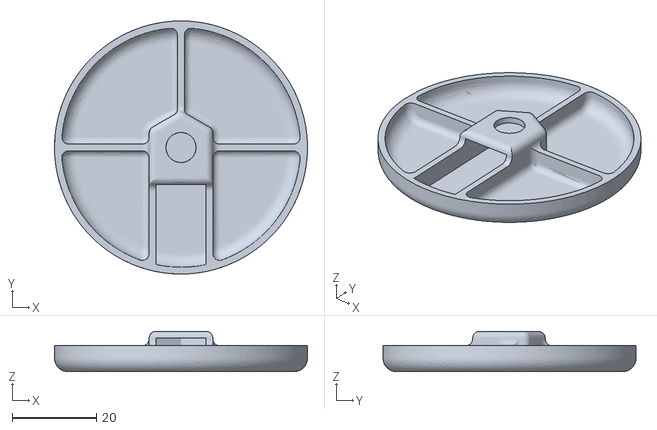
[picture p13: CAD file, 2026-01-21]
MMC60-Switch/Build_Files/3D_Printing_Files/Custom_Tops/RFS_B_Button.stl
60.0 x 60.0 x 9.55

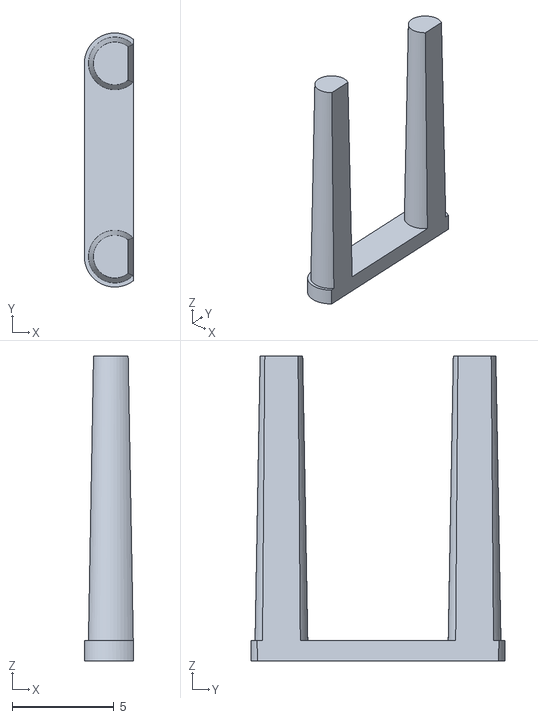
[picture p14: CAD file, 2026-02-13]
MMC60-Switch/Build_Files/3D_Printing_Files/RFS_Pins.stl
2.43 x 12.5 x 15.0

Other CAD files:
Interact-Switch/Build_Files/3D_Printing_Files/Alternate_Caps/ButtonCap_Octagon.STL
Light-Touch-Switch/Design_Files/CAD_Design_Files/Step/LTS_Pin_v0.step
MMC60-Switch/Design_Files/CAD_Design_Files/MMC60 Switch v111.step
Interact-Switch/Build_Files/3D_Printing_Files/Alternate_Caps/ButtonCap_Arrow.STL
Interact-Switch/Build_Files/3D_Printing_Files/Alternate_Caps/ButtonCap_Circle.STL
Interact-Switch/Build_Files/3D_Printing_Files/Alternate_Caps/ButtonCap_Dome.STL
Interact-Switch/Build_Files/3D_Printing_Files/Alternate_Caps/ButtonCap_Dots_Circles.STL
Interact-Switch/Build_Files/3D_Printing_Files/Alternate_Caps/ButtonCap_Dots_Wide.STL
Interact-Switch/Build_Files/3D_Printing_Files/Alternate_Caps/ButtonCap_Lines.STL
Interact-Switch/Build_Files/3D_Printing_Files/Alternate_Caps/ButtonCap_Lines_VeryWide.STL
Interact-Switch/Build_Files/3D_Printing_Files/Alternate_Caps/ButtonCap_Lines_Wide.STL
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

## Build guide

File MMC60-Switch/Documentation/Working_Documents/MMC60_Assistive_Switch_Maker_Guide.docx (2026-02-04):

# Overview

This document contains the necessary information to build the device.

# Maker Checklist

This list provides an overview of the steps required to build and deliver the device.

## Maker To Do List

- Read through the Assembly Guide to become familiar with required components, tools, supplies, and safety gear and overall assembly steps.
- Talk to User about customization options (e.g., color, any special requests, etc.)
- Order hardware components
- Gather tools, supplies, and safety equipment.
- Assemble the device
- Test device
- Print “User Guide”

## Items to Give to User

- Assembled, tested device
- “User Guide”

# Tool List

# Customization Guide

The device can be printed in the user’s desired colour.

# 3D Printing Guide

## 3D Printing Summary

Metrics | Single Unit
Total Print Time (min) | 1h10m
Total Number of Components | 1
Typical Total Mass (g) | 13
Typical Number of Print Setups | 1

## 3D Printing Settings

Print File Name | Qty | Total Print Time (hr:min) | Mass (g) | Infill (%) | Support(Y/N) | Layer Height/ Nozzle Diameter(mm) | Notes
Tetra-Pack-Opener.stl | 1 | 1:10 | 13 | 15 | N | 0.2/0.4

## Post-Processing

- Add any processes that must be done after print such as removing supports

## Examples of Quality Prints

Photo of Device

# Assembly Guide

## Required Components

<Insert a photo with all components of the device laid out and labelled with number that correspond to the numbers in the cell to the right. Add appropriate Alt text> | BOM

## Required Tools

## Required Personal Protective Equipment (PPE)

### Step 1: Gather materials and tools

<Description>

<Insert photo here. Make sure to add appropriate alt text>

### Step 2: <Step Summary>

<Description>

<Insert photo here. Make sure to add appropriate alt text >

### Step 3: <Step Summary>

<Description>

<Insert photo here. Make sure to add appropriate alt text >

<Add additional steps as necessary>

# Testing

© 2022 by <Author>. This work is licensed under the CC BY SA 4.0 License: http://creativecommons.org/licenses/by-sa/4.0 Files available at <Replace with MMC Github Link> Page 1 of 1

V1.0 | JANUARY 2023 Device-Name maker Guide

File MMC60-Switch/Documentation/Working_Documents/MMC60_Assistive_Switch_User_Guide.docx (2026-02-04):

## Introduction

<Help Text>

## Features

<Labelled photo / line drawing>

## Usage

<Basic usage steps / instructions>

## Compatibility

## Specifications

<List of overall dimensions, weight,

## Cleaning

<Instructions for how to clean / disinfect / sterilize device>

© 2022 by Neil Squire. This work is licensed under the CC BY SA 4.0 License: http://creativecommons.org/licenses/by-sa/4.0 Files available at <MMC Project Library Link> Page 2 of 3

VX.X | <MONTH> <YEAR> <Device Name> user Quick Guide

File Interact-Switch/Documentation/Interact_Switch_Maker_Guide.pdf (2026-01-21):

V2.0 | July 2025

## Interact Switch

## MAKER GUIDE

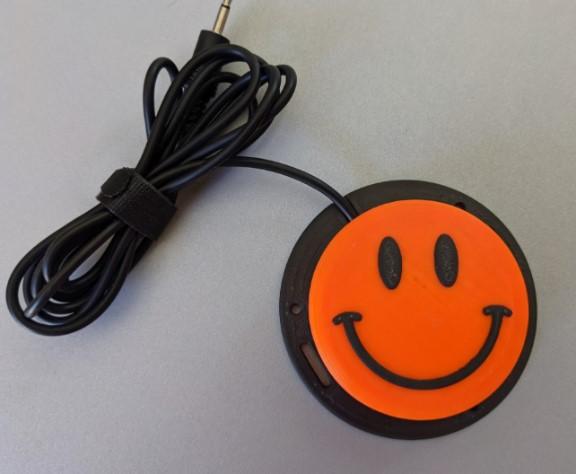
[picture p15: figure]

© 2025 by Neil Squire. (https://neilsquire.ca/)
This work is licensed under the CC BY SA 4.0 License: http://creativecommons.org/licenses/by-sa/4.0
Files available at https://github.com/makersmakingchange/Interact-Switch | Page 1 of 14

### Overview

This document contains the necessary information to build the Interact Switch, a large customizable switch with a low activation force.

## MAKER GUIDE

Files available at https://github.com/makersmakingchange/Interact-Switch | Page 2 of 14

### Contents

Overview | 1
Maker Checklist | 3
Maker To Do List | 3
Items to Give to User | 3
Attribution | 3
Tool List | 4
Tools / Equipment | 4
Supplies | 4
Personal Protective Equipment (PPE) | 4
Customization Guide | 5
3D Printing Guide | 7
3D Printing Summary | 7
3D Printing Settings | 7
Post-Processing | 8
Examples of Quality Prints | 8
Building the Interact Switch | 9
Required Components | 9
Required Tools and Supplies | 9
Required Personal Protective Equipment (PPE) | 9
Assembly Steps | 10
Testing | 14
Troubleshooting | 14

## MAKER GUIDE

Files available at https://github.com/makersmakingchange/Interact-Switch | Page 3 of 14

### Maker Checklist

This list provides an overview of the steps required to build and deliver the Interact Switch.

### Maker To Do List

Read through the Maker Guide to become familiar with required components, tools, supplies, safety gear, and overall assembly steps.
Talk to the User about customization options
- What colour(s) would they like the topper and/or topper pattern to be printed in?
- Which topper would they like to have? There are a variety of toppers available with different patterns and textures.
- How would they like to receive the “User Guide”? (PDF or physical copy)
Order hardware components
Gather tools, supplies, and safety equipment.
Assemble the device
Test the Interact Switch

### Items to Give to User

Interact Switch
User Guide

### Attribution

The Interact Switch (https://github.com/mwturvey/InteractSwitch/tree/master) design by Mike Turvey (https://github.com/mwturvey) is used under CC-BY 4.0. (https://creativecommons.org/licenses/by/4.0/) Instructions adapted from Original Interact Switch Assembly Instructions (https://docs.google.com/document/d/1uWRKXmApZUaSo1I0oyyFrAfncziYsd2_8ai8dunogJs/edit?usp=sharing) by Mike Turvey, (https://github.com/mwturvey) used under CC-BY 4.0. (https://creativecommons.org/licenses/by/4.0/)

Due to changes made to make the switch compatible with the #4 sheet metal screws, the Base and Switch holder are no longer compatible with the original parts.

## MAKER GUIDE

Files available at https://github.com/makersmakingchange/Interact-Switch | Page 4 of 14

### Tool List

### Tools / Equipment

Tool ID | Description | Required / Recommended | Notes
T01 | Wire Strippers | Required | Stripping insulation from the cable
T02 | Soldering Iron | Required | Soldering the Cable to the switch
T03 | Phillips Screwdriver | Required | Attaching the base to the top

### Supplies

Supplies ID Description | Quantity | Notes
S01 | Solder | Roughly 1 inch | To attach the mono cable to the button

### Personal Protective Equipment (PPE)

PPE ID | Description | Notes
P01 | Safety Glasses | To keep flying debris out of your eyes

## MAKER GUIDE

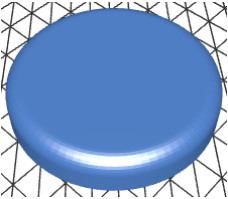
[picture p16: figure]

Files available at https://github.com/makersmakingchange/Interact-Switch | Page 5 of 14

### Customization Guide

The device can be printed in the user’s desired colour.

There are over 12 different button caps available in the GitHub repository, and some projects such as the Open Playback Recorder have custom Interact Switch caps that match buttons on the device.

When printing the textured button caps, a filament change can be done to print the textured part of the cap in a different colour from the main body, increasing contrast. This can also be done automatically on printers that support multi-material printing.

The plain, ‘default’ button topper can be seen below, and the other options included in the Interact Switch Repository are listed in the table below.

## MAKER GUIDE

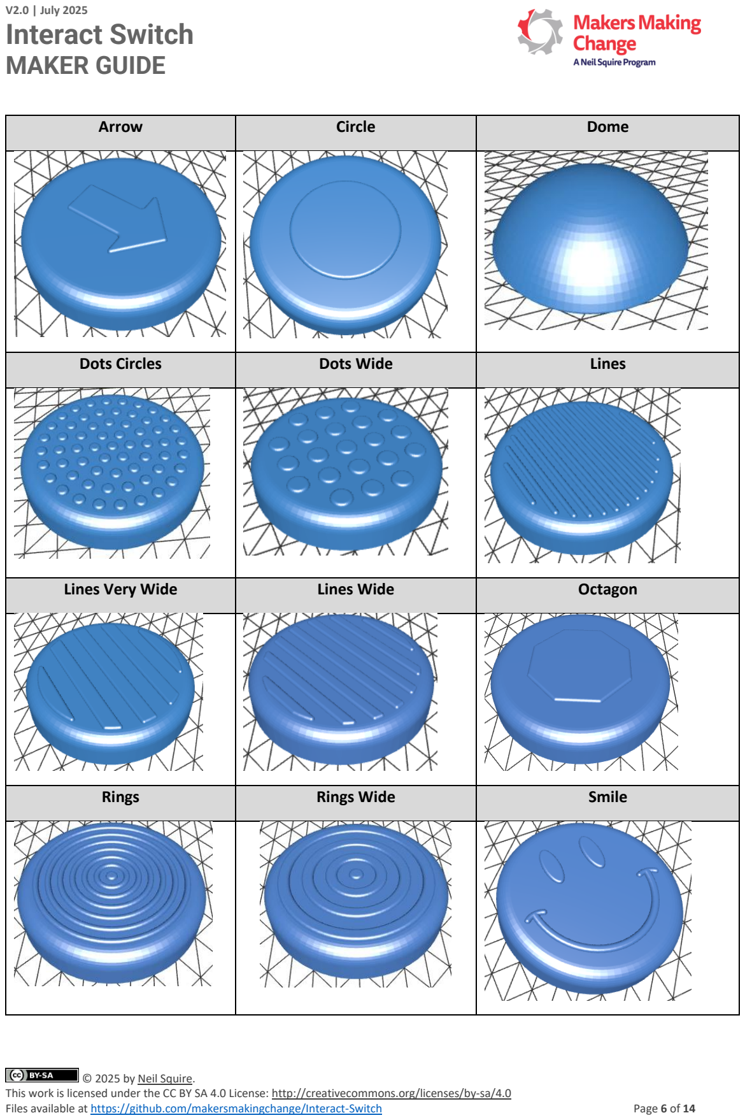
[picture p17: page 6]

Files available at https://github.com/makersmakingchange/Interact-Switch | Page 6 of 14
Arrow | Circle | Dome
Dots Circles | Dots Wide | Lines
Lines Very Wide | Lines Wide | Octagon
Rings | Rings Wide | Smile

## MAKER GUIDE

Files available at https://github.com/makersmakingchange/Interact-Switch | Page 7 of 14

### 3D Printing Guide

The device was originally printed on a Bambu P1S using Bambu Studio using the default profile.

### 3D Printing Summary

Metrics | Single Unit
Total Print Time (hour min) | 1h8min
Total Number of Components | 4
Typical Total Mass (g) | 35
Typical Number of Print Setups | 3

### 3D Printing Settings

Note that the 3D printing material should be assumed to be PLA unless otherwise noted in the table below.

Print File Name | Qty | Total Print Time (hr:min) | Mass (g) | Infill (%) | Suppor (Y/N) | Layer Height/ Nozzle Diameter(mm) | Notes
Interact_Switch_Base.stl | 1 | 0:32 | 17 | 20 | N | 0.2/0.4
Interact_Switch_Cap_Plain.stl | 1 | 0:25 | 14 | 20 | N | 0.2/0.4 | Default cap; others are available
Interact_Switch_Holder.stl | 1 | 0:09 | 3 | 20 | N | 0.2/0.4
Interact_Switch_Insert_0.6mm.stl | 1 | 0:02 | 1 | 20 | N | 0.1/0.4 | Print with 0.1 mm layer height if printing an odd numbered insert (i.e. a 0.5 mm or 0.9 mm)
Interact_Switch_Solder_Jig.stl | 1 | 0:25 | 12 | 20 | N | 0.2/0.4 | Optional

Depending on the tolerances of your printer, you may have to print a different switch insert than the
0.6mm insert. The insert is the part that makes the cap press the switch in the base, and depending on the tolerances of your printer, this distance might be too close or too far for the 0.6mm insert. The repository includes inserts from 0.2 to 1.5mm and it may take a few tries to find the right one that works for your printer.

## MAKER GUIDE

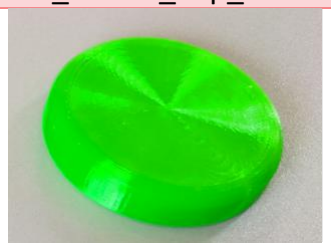
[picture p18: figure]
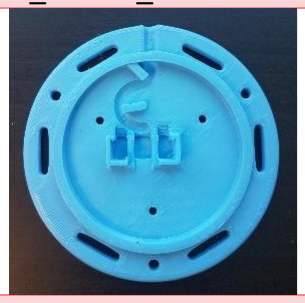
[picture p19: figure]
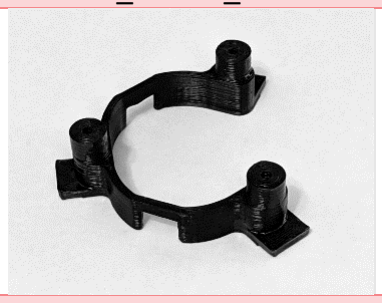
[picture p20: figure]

Files available at https://github.com/makersmakingchange/Interact-Switch | Page 8 of 14

### Post-Processing

Inspect the 3D printed parts for any printing defects, sharp edges, or burrs. Sharp edges and burrs can be removed with sanding or deburring tools.

### Examples of Quality Prints

Compare your 3D prints to the images here. If there are significant differences, you may need to reprint the part.

Interact Switch
Interact_Switch_Base.stl | Interact_Switch_Cap_Plain.stl | Interact_Switch_Holder.stl

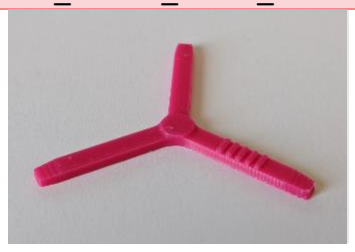
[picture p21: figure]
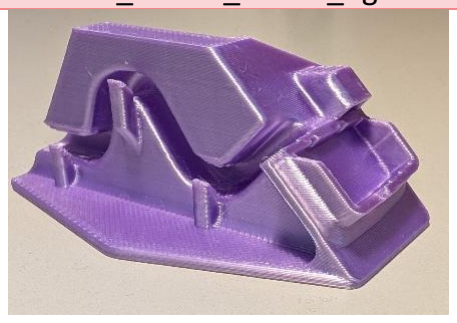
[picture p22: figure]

Interact_Switch_Insert_0.6mm.stl | Interact_Switch_Solder_Jig.stl

## MAKER GUIDE

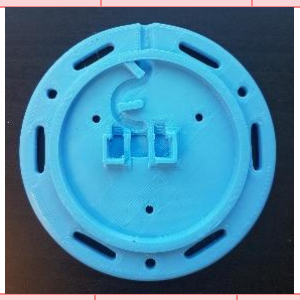
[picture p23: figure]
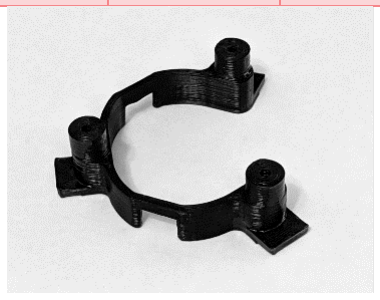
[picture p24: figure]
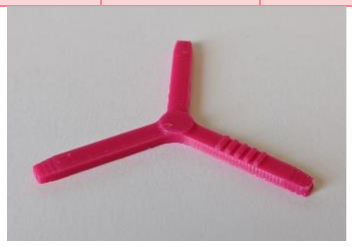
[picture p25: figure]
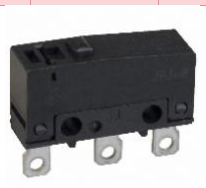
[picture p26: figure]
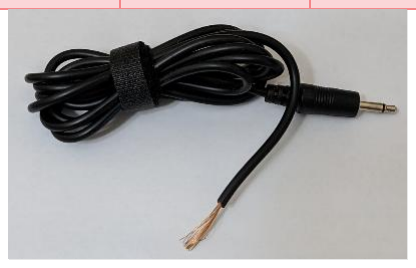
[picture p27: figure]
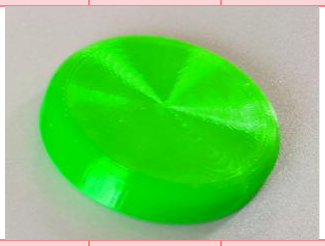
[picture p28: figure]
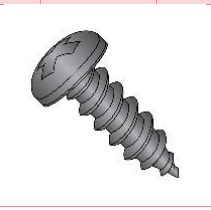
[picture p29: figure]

Files available at https://github.com/makersmakingchange/Interact-Switch | Page 9 of 14

### Building the Interact Switch

Required Components
Interact Switch
A01 | Switch Base | QTY: 1 | A02 | Button Cap Holder
QTY: 1 | A03 | Button Cap
Insert

QTY: 1

A04 | Button Cap | QTY: 1 | A05 | Limit Switch
QTY: 1 | A06 | Mono
Cable

QTY: 1

A07 #4 Sheet Metal Screw

QTY: 3

Required Tools and Supplies
- Wire Strippers
- Soldering Iron
- Screwdriver

Required Personal Protective Equipment (PPE)
- Safety Glasses

## MAKER GUIDE

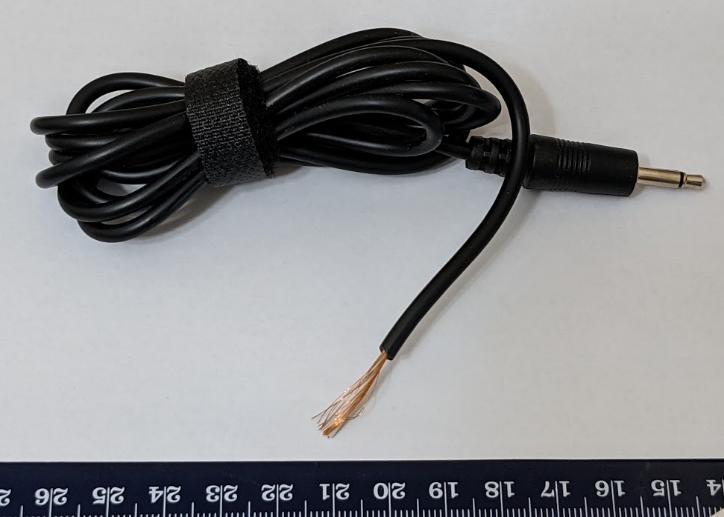
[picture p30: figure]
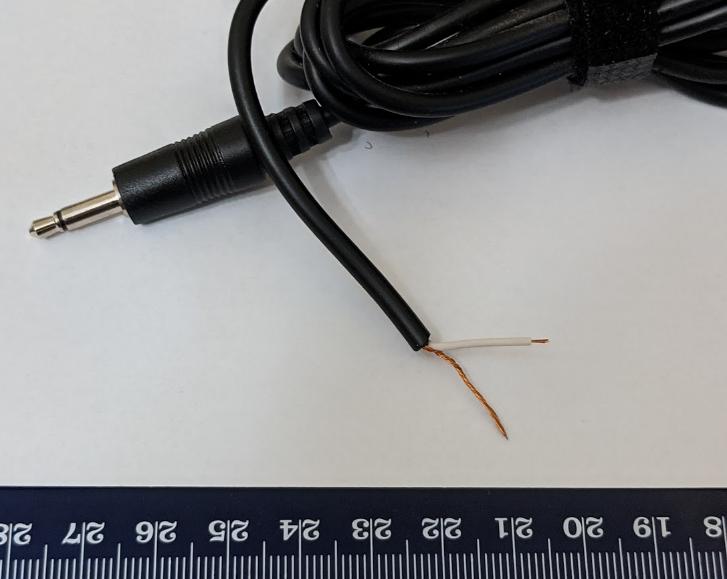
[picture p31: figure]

Files available at https://github.com/makersmakingchange/Interact-Switch | Page 10 of 14

Assembly Steps

Step 1: Prep Cable
Cut off and discard one of the plugs from the mono audio cable.

Use the wire strippers to carefully remove about 15 mm of the outer insulation from the end.

Step 2: Prep Cable Wires
Twist the copper strands together into a single wire.

Use the wire strippers to remove roughly 5 mm of insulation from the other wire.

(Note: Your cable may differ. If there are two wires with insulation, strip 5 mm from the end of each wire.)

## MAKER GUIDE

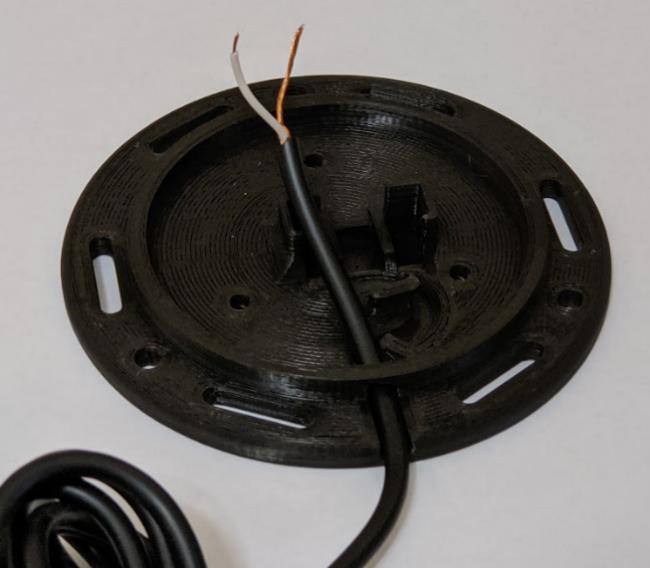
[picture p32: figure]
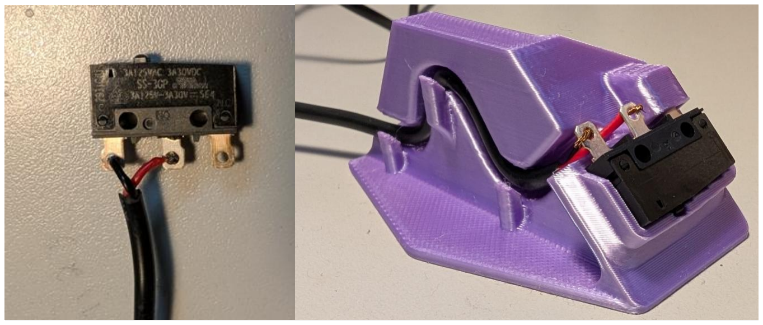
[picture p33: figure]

Files available at https://github.com/makersmakingchange/Interact-Switch | Page 11 of 14
Step 3: Thread Cable into Switch Base
Thread the cable through the hole in the Switch Base. You will not be able to do this after you solder the limit switch onto the wire.
Step 4: Solder Wires to Switch
Solder the wires into the switch in the position shown below. The optional soldering jig can be used to hold the cable and switch in place, and to isolate the correct terminals to solder to.

Note: Solder the two leads closest to the button on the switch.

Test: plug your switch into a switch activated device and push the button on the limit switch

## MAKER GUIDE

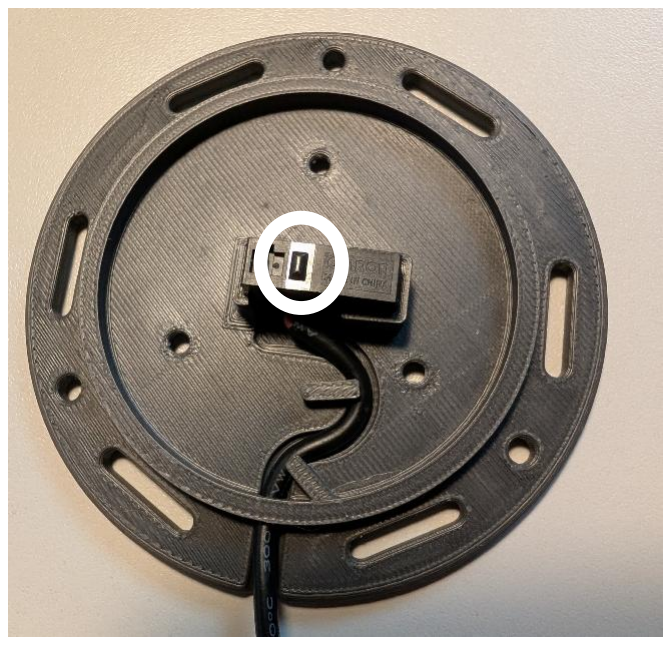
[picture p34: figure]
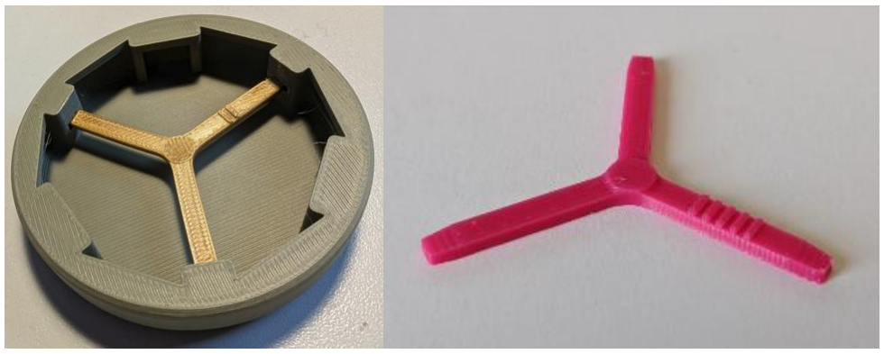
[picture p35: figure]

Files available at https://github.com/makersmakingchange/Interact-Switch | Page 12 of 14
Step 5: Position Switch in Base
Place the limit switch into the Switch Base as shown.

For the orientation of the switch, when the cable is coming towards you, the button on the limit switch should be offset to the left. Make sure that no wires are stuck underneath, preventing the limit switch from going all the way down.

Push the cable in the slot as shown in the picture.

Step 6: Assemble Button Cap
Turn the Button Cap over and insert the Button Cap Insert. If you’re unsure which size to use, try starting with 0.6 mm. The lines on the button insert should be facing up, with the print surface facing down towards the cap. The raised section where all three legs on the insert join should be visible.

## MAKER GUIDE

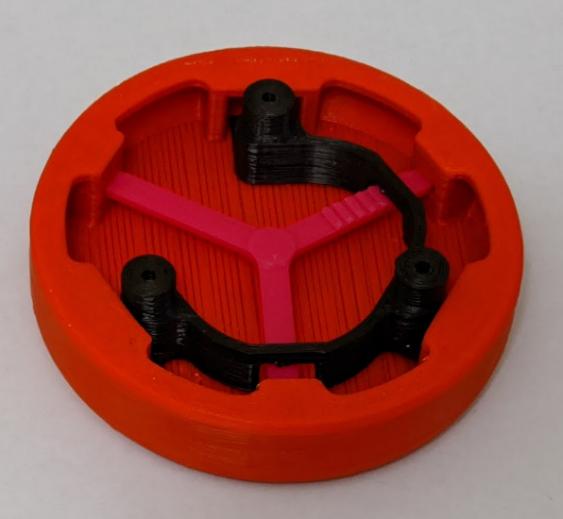
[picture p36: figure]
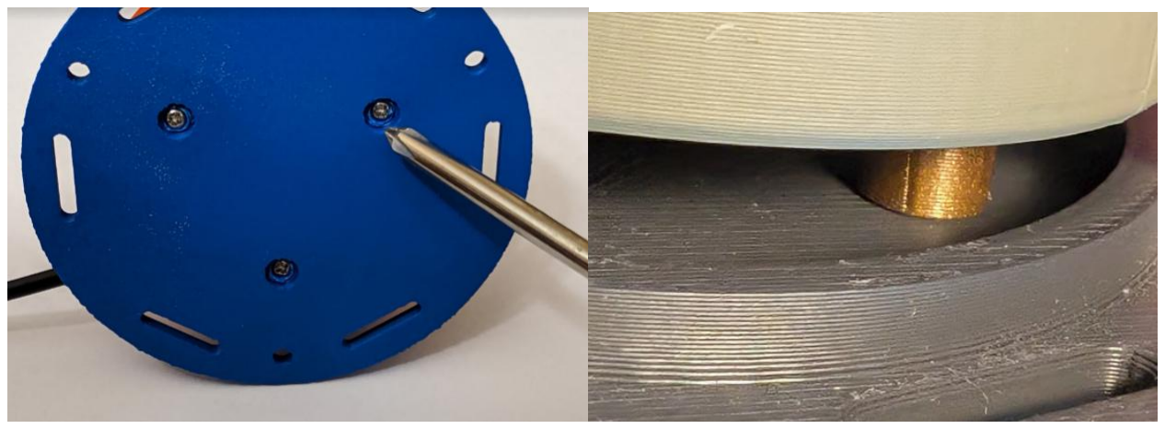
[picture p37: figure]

Files available at https://github.com/makersmakingchange/Interact-Switch | Page 13 of 14
Step 7: Finalize Button Cap Assembly
Insert the Button Cap Holder into the Button Cap Assembly. The orientation of the “open” side doesn’t matter.

Note: for smoother switch action, sand the edges of the Button Cap Holder where it rubs on the switch.

Step 8: Assemble Switch
Align the three posts of the Switch Cap Holder to the three holes in the Switch Base. Secure the Switch Cap Holder to the Switch Base using three screws. Tighten them until the Switch Cap holder is firmly against the base.

Note: Be careful not to over tighten the screws. Tighten them until you notice the resistance increases and the Switch Cap Holder is firmly against the Switch Base.

## MAKER GUIDE

Files available at https://github.com/makersmakingchange/Interact-Switch | Page 14 of 14

### Testing

The last thing to do is test your switch. If this is your first switch, you’ll likely need to test it out and figure out the best size of Switch Cap Insert to use.

The first thing to do to test a switch is to push it a lot. Tap it everywhere, repeatedly. Every time you push it, you should hear it click down and click as it goes back up. It should never stick. If you wiggle the top, it should move some, but it shouldn’t feel like it’s rattling around. Next, plug the switch into a switch activated device and make sure that it works.

### Troubleshooting

Problem | Solution
The switch cap is too loose and rattles around easily. | Use a larger/ thicker Switch Cap Insert.
Switch doesn’t make any noise when pushed. | Use a smaller/ thinner Switch Cap Insert. An insert that is too big can cause the limit switch to be always depressed. When this is the case, you’ll often hear the limit switch “click” closed when you’re screwing everything together, but it won’t ever click open.
Switch sticks/ doesn’t always go back up. | Use a smaller/ thinner Switch Cap Insert. You may likely need just one size thinner.
Switch makes clicking noise, but the switch activated device isn’t activating | • Test the switch activated device with a switch known to work, just to make sure it’s working fine. • Check that the plug is firmly plugged into the device • The solder connection may be bad and need to be re-soldered. • There may be an internal break in the wire, and you will need to replace it. This is a particularly common failure point for an older switch.

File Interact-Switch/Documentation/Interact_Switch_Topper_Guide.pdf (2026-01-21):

V2.0 | July 2025

## Interact Switch

## TOPPER GUIDE

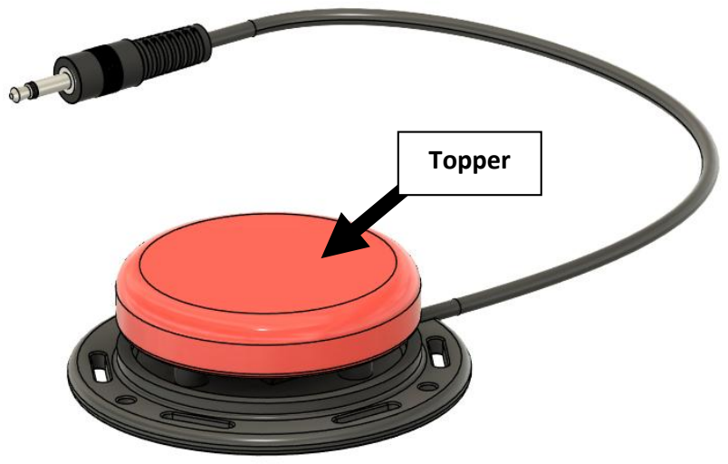
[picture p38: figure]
Topper

© 2025 by Neil Squire. (https://neilsquire.ca/)

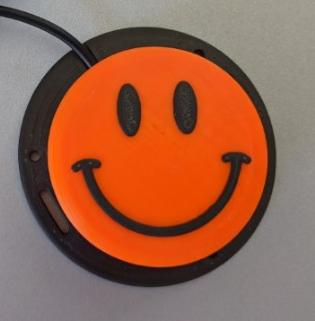
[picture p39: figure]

This work is licensed under the CC BY SA 4.0 License: http://creativecommons.org/licenses/by-sa/4.0
Files available at https://github.com/makersmakingchange/Interact-Switch | Page 1 of 2

### Overview

The Interact Switch is available with several different Switch Tops. Using different colors and textures can help a user distinguish between switches by sight or feel. The plain, ‘default’ button topper can be seen below, and the other options included in the Interact Switch Repository are listed in the table on the next page.

Generally, it is also possible and easy to print toppers in different colors. It is also possible to print a topper in multiple colors based on the height. This is illustrated below with a Smile Topper that has the main portion printed in orange and the raised portion printed in black.

## Interact Switch

## TOPPER GUIDE

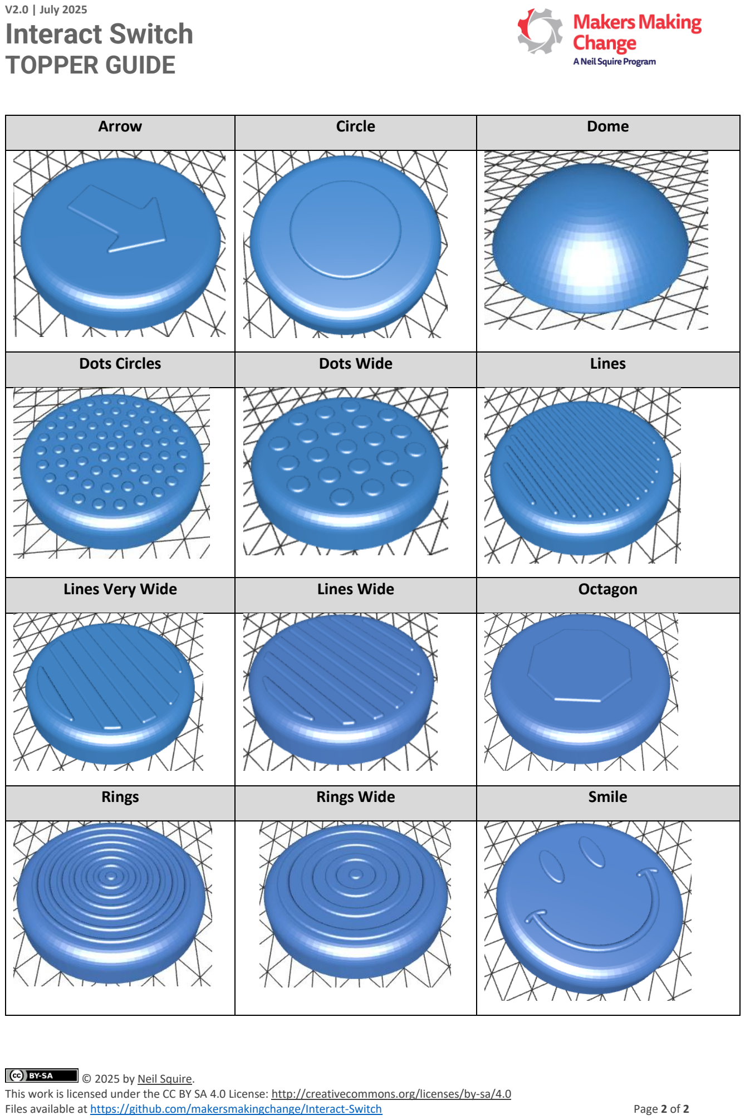
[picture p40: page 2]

V2.0 | July 2025

© 2025 by Neil Squire. (https://neilsquire.ca/)
This work is licensed under the CC BY SA 4.0 License: http://creativecommons.org/licenses/by-sa/4.0
Files available at https://github.com/makersmakingchange/Interact-Switch | Page 2 of 2
Arrow | Circle | Dome
Dots Circles | Dots Wide | Lines
Lines Very Wide | Lines Wide | Octagon
Rings | Rings Wide | Smile

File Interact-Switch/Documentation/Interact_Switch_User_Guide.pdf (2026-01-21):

## Interact Switch

## USER GUIDE

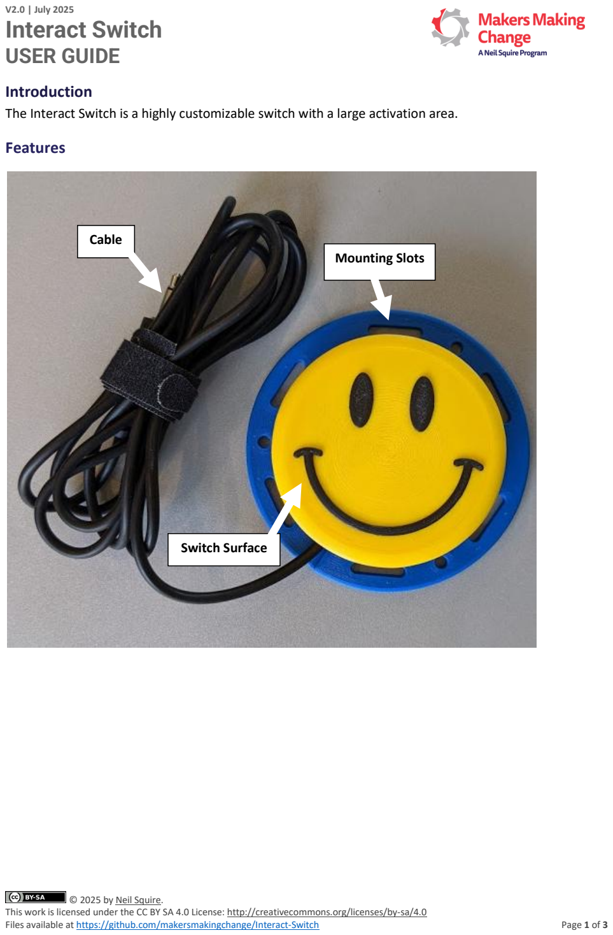
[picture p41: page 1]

V2.0 | July 2025

© 2025 by Neil Squire. (https://neilsquire.ca/)
This work is licensed under the CC BY SA 4.0 License: http://creativecommons.org/licenses/by-sa/4.0
Files available at https://github.com/makersmakingchange/Interact-Switch | Page 1 of 3

### Introduction

The Interact Switch is a highly customizable switch with a large activation area.

### Features

Mounting Slots

Switch Surface

Cable

## USER GUIDE

Files available at https://github.com/makersmakingchange/Interact-Switch | Page 2 of 3

### Specifications

Item | Interact Switch
Size (Length x Width x Height) [mm] | 85x85x30
Mass [g] | 60
Press Force [g] | 35

### Compatibility

The Interact Switch is compatible with any accessible device that uses a standard 3.5mm mono jack switch.

### Usage

Initial Setup
Place the Interact Switch where it works best for the user. Hook and loop fastener (e.g., VELCRO) or a non-slip mat (e.g., DYCEM) can be used to prevent it from sliding on a surface, and the holes and slots around the rim can be used to screw, cable tie, or otherwise fasten it into place.

Regular Use
When the Interact Switch is connected to the device, a press of the switch will register as a button press on the connected port.

Takedown / Storage
When not in use, the Interact Switch should be stored in a cool place out of direct sunlight.

### Care

The Interact Switch is made of 3D printed plastic. Exposure to high heat may cause warping and/or negatively affect function. Extended exposure to sunlight will also weaken the plastic on the device.

The Interact Switch contains electronics and is not waterproof. If the device becomes wet, make sure it is off and do not use it until it has completely dried. It may help to open any electronic enclosures to speed up drying and ensure it has completely dried.

Cleaning
The Interact Switch can be wiped with a damp cloth. The Interact Switch can also be cleaned by scrubbing with warm water and dish soap, but should not be submerged in water. Do not use hot water or clean in a dishwasher.

## USER GUIDE

Files available at https://github.com/makersmakingchange/Interact-Switch | Page 3 of 3

### Disposal

PLA filament may be industrially compostable in your area. Check with your waste management company if PLA can be composted or must be thrown in the garbage.

Disassemble the Interact Switch and separate out the recyclable and compostable components, and those that must be thrown out. Electronics and batteries should be disposed of following your local waste management guidelines.

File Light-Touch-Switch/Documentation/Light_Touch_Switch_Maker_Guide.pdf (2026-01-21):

V1.0.0 | June 2024

## Light Touch Switch

## MAKER GUIDE

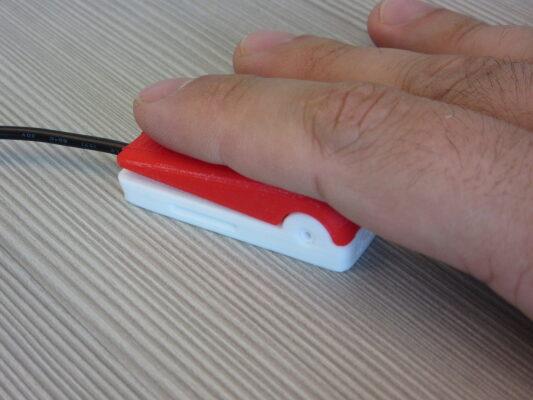
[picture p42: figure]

© 2024 by Neil Squire. (https://neilsquire.ca/)
This work is licensed under the CC BY SA 4.0 License: http://creativecommons.org/licenses/by-sa/4.0 Files available at https://github.com/makersmakingchange/Light-Touch-Switch

### Overview

This document contains the necessary information to build the Light Touch Switch, a cost-effective 3D printable accessibility switch for people with physical disabilities.

## MAKER GUIDE

© 2024 by Neil Squire. (https://neilsquire.ca/)

### Contents

Overview | 1
Maker Checklist | 4
Maker To Do List | 4
Items to Give to User | 4
Tool List | 5
Tools / Equipment | 5
Supplies | 5
Personal Protective Equipment (PPE) | 5
Customization Guide | 6
3D Printing Guide | 6
3D Printing Summary | 6
3D Printing Settings | 6
Post-Processing | 6
Examples of Quality Prints | 7
Maker Component List | 8
Assembly Guide | 8
Required Components | 8
Required Tools and Supplies | 8
Required Personal Protective Equipment (PPE) | 8
Assembly Steps | 9
Step 01: Remove print supports | 9
Step 02: Trim switch leads | 9
Step 03: Straighten remaining switch leads | 9
Step 04: Trim mounting lugs | 10
Step 05: Cut mono cable | 10
Step 06: Strip the mono cable | 10
Step 07: Strip the inner wire(s) | 11

## MAKER GUIDE

© 2024 by Neil Squire. (https://neilsquire.ca/)

Step 08: Wrap wires around switch leads | 11
Step 09: Fix orientation of cable | 11
Step 10: Solder switch joints | 12
Step 11: Test the switch | 12
Step 12: Apply glue to button base | 12
Step 13: Place switch in button base | 13
Step 14: Seal the cable with glue | 13
Step 15: Insert the button top and pin | 13
Step 16: Trim the pin | 14
Testing | 14
Troubleshooting | 14

## MAKER GUIDE

© 2024 by Neil Squire. (https://neilsquire.ca/)

### Maker Checklist

This list provides an overview of the steps required to build and deliver the Light Touch Switch.

### Maker To Do List

Read through the Maker Guide to become familiar with required components, tools, supplies, safety gear, and overall assembly steps.
Talk to the User about customization options
- What colour they would like the switch to be
- If they would like different parts to be different colours
- How they would like to receive the “User Guide” (PDF or physical copy) Order hardware components
Gather tools, supplies, and safety equipment.
Assemble the device
Test the Light Touch Switch
Print “User Guide” (if the User would like a physical copy)

### Items to Give to User

Built and tested Light Touch Switch
“User Guide”

## MAKER GUIDE

© 2024 by Neil Squire. (https://neilsquire.ca/)

### Tool List

### Tools / Equipment

Tool ID | Description | Required / Recommended | Notes
T01 | Wire cutters / strippers | Required | Cutting and stripping the mono cable wires.
T02 | Flush cutter | Required | Trimming the tactile switch and button pin.
T03 | Soldering iron and stand | Required | Soldering the mono cable to the tactile switch.
T04 | Hot glue gun | Required | Securing the tactile switch and mono cable to the button base.
T05 | Needle nosed pliers | Required | Removing support material from 3D prints. Wrapping wires from mono jack around switch leads.
T06 | 3D printed switch jig | Recommended | A 3D printed jig that holds the switch and mono cable while soldering.
T07 | Switch testing device | Required | A device to test if the switch works. This could be a switch tester, (https://github.com/makersmakingchange/Simple-Switch-Tester) a continuity tester, or a working switch adapted device.

### Supplies

Supplies ID Description | Quantity | Notes
S01 | Solder | A small amount | Soldering the mono cable to the tactile switch.
S02 | Hot glue | A small amount | Holds the tactile switch in place and provides strain relief on the cable.

### Personal Protective Equipment (PPE)

PPE ID | Description | Notes
P01 | Safety glasses | Eye protection while trimming parts and soldering.

## MAKER GUIDE

© 2024 by Neil Squire. (https://neilsquire.ca/)

### Customization Guide

The device can be printed in the user’s desired colour. The user may want specific colours, and may want the 3D printed parts in different colours.

### 3D Printing Guide

The device was originally printed on an Ender 3-S1 using Cura as the slicer software using the standard printer profile. Print time and the number of print setups may differ significantly, depending on your printer.

### 3D Printing Summary

Metrics | Single Unit
Total Print Time (min) | 1h 09m
Total Number of Components | 3
Typical Total Mass (g) | 8
Typical Number of Print Setups | 1
Note that the above summary does not include the optional switch jig.

### 3D Printing Settings

All parts should be printed in the orientation they appear when imported into the slicer.

Print File Name | Qty | Total Print Time (hr:min)

Mass
(g)

Infill
(%)

Support(Y/N) Layer Height/ Nozzle
Diameter(mm)

Notes

LTS_Base_v1.0.stl | 1 | 00:33 | 3 | 20 | N | 0.2/0.4
LTS_Top_v1.0.stl | 1 | 00:33 | 4 | 20 | Y | 0.2/0.4
LTS_Pin_v0.1.stl | 1 | 00:04 | 1 | 20 | N | 0.2/0.4

Optional Parts

Switch_Jig_12mm_
V1.0.stl
1 | 00:35 | 4 | 20 | N | 0.2/0.4

### Post-Processing

Inspect the 3D printed parts for any printing defects, sharp edges, or burrs. Sharp edges and burrs can be removed with sanding or deburring tools.

## MAKER GUIDE

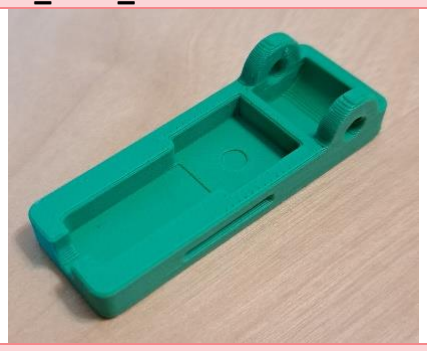
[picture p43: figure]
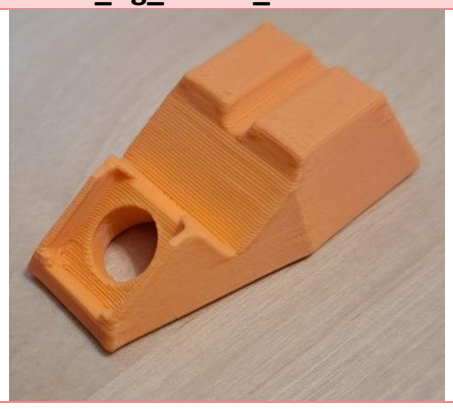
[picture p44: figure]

© 2024 by Neil Squire. (https://neilsquire.ca/)

### Examples of Quality Prints

Compare your 3D prints to the images here. If there are significant differences, you may need to reprint the part.

Light Touch Switch
LTS_Base_v1.0.stl | LTS_Top_v1.0.stl | LTS_Pin_v0.1.stl

Switch_Jig_12mm_V1.0.stl

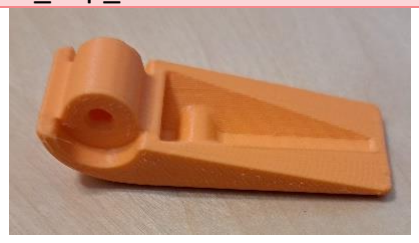
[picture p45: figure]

## MAKER GUIDE

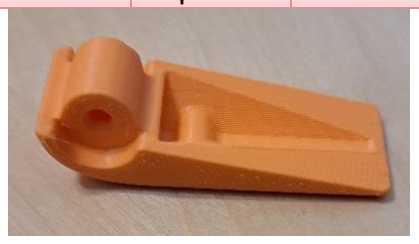
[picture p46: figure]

© 2024 by Neil Squire. (https://neilsquire.ca/)

### Maker Component List

Light Touch Switch Parts
A01 Tactile
switch
QTY: 1 | A02 | Mono cable | QTY: 1 | A03 | Button base

QTY: 1

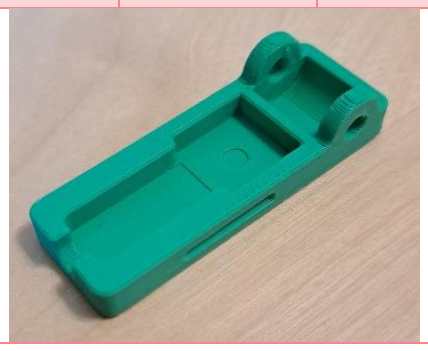
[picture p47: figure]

A04 Button
cap

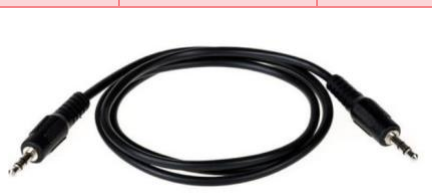
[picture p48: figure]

QTY: 1 | A05 | Button pin | QTY: 1

### Assembly Guide

### Required Components

### Required Tools and Supplies

- Wire cutter / stripper
- Flush cutter
- Soldering iron and stand
- Hot glue gun
- Needle nosed pliers
- Switch jig (optional)
- Switch testing device (switch tester, (https://github.com/makersmakingchange/Simple-Switch-Tester) a continuity tester, or a working switch adapted device)

### Required Personal Protective Equipment (PPE)

- Safety glasses

## MAKER GUIDE

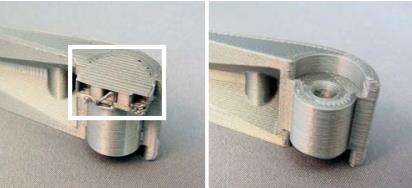
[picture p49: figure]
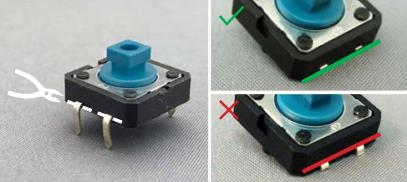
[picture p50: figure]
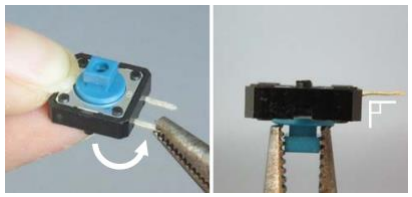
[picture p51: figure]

© 2024 by Neil Squire. (https://neilsquire.ca/)

### Assembly Steps

Step 01: Remove print supports
Remove the support material from the button cap (A04). Use needle nosed pliers, if necessary.
Step 02: Trim switch leads
Use a flush cutter to trim off the leads on one side of the tactile switch. Make sure the leads are cut flush against the side of the switch and do not extend below the bottom of the switch.
Step 03: Straighten remaining switch leads
Straighten the remaining switch leads, ensuring they stick straight out from the side of the switch. Use the needle nosed pliers, if necessary.

## MAKER GUIDE

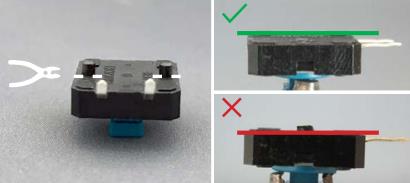
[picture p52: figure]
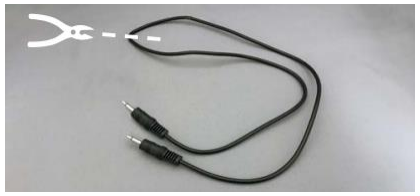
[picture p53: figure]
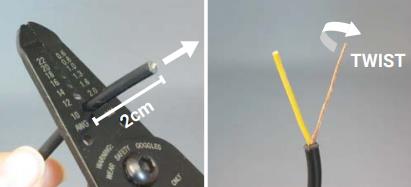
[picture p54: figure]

© 2024 by Neil Squire. (https://neilsquire.ca/)

Step 04: Trim mounting lugs
Use the flush cutters to trim the plastic mounting lugs (the plastic cylinders) off the bottom of the switch. Make sure the lugs are cut flush, with no remaining bumps.
Step 05: Cut mono cable
If using a two-ended mono cable, cut it in half. If the mono cable only has one end, skip this step.
Step 06: Strip the mono cable
Use the wire strippers to strip about 2 cm from the end of the mono cable, exposing the inner two wires. Twist the stranded wire together.

The inner wire colours may differ depending on the mono cable. Some may have one stranded wire and one coated wire, or have two coated wires. If you have two coated wires, do not twist any wires together at this step.

## MAKER GUIDE


© 2024 by Neil Squire. (https://neilsquire.ca/)

Step 07: Strip the inner wire(s)
Strip about 1.5 cm of insulation from the end of the inner coated wire. Twist the wire strands from that wire together. Repeat this for the other coated wire, if both inner wires were coated.

The wire strands from each inner wire should not be touching each other or twisted together.

Step 08: Wrap wires around switch leads
Hold the mono cable behind the switch and wrap one wire around one switch lead and the other wire around the other switch lead. Which wire is connected to which lead does not matter, just make sure the wires and leads do not touch each other, or the switch will be short circuited. Needle nosed pliers may help with wrapping the wires.
Step 09: Fix orientation of cable
Hold the switch in place and bend the mono cable around so it sits between the leads of the switch.

## MAKER GUIDE


© 2024 by Neil Squire. (https://neilsquire.ca/)

Step 10: Solder switch joints
Place the switch and cable into the switch jig, then use a soldering iron to solder the wires to the switch leads, indicated in the white rectangle. Once soldered, the wires should not slip off the switch leads.
Step 11: Test the switch
Test that the switch works properly. The switch should consistently activate only when it is pressed (when the blue part of the tactile switch is pressed down).

Potential methods for testing the switch works include using a dedicated switch tester, using a continuity tester, or using a switch adapted device you know works.

Detailed testing and troubleshooting information can be found in the Testing and Troubleshooting sections.

Step 12: Apply glue to button base
Use a hot glue gun to add a small drop of glue on the inside of the square recess in the button base.

## MAKER GUIDE


© 2024 by Neil Squire. (https://neilsquire.ca/)

Step 13: Place switch in button base
Place the tactile switch and mono cable into the button base, with the switch sitting on the drop of glue from the previous step. Make sure the switch sits flat and level inside the button base.

If the switch is not level, push it down while the glue is still warm. If it cannot be set level, remove the switch, check to see the mounting lugs and leads were trimmed flush, remove any leftover glue, and glue it back in with a smaller drop of glue.

Step 14: Seal the cable with glue
Fill the recess around the mono cable with hot glue to seal the cable. Do not overfill or the switch may not function properly. The glue should not come past the top edge of the button base.
Step 15: Insert the button top and pin
Slide the button top onto the base. Test which side of the button pin fits best, then insert it all the way in. The pin should be snug so it does not fall out, but not too tight to prevent the top from moving or be inserted.

## MAKER GUIDE


© 2024 by Neil Squire. (https://neilsquire.ca/)

Step 16: Trim the pin
Use the flush cutters to trim the pin flush with the side of the base. If the cut edge of the pin is sharp, or the pin feels like it will slip out, secure it with a small drop of hot glue.

Congratulations, your Light Touch Switch is now complete!

### Testing

Testing the switch involves checking that it only activates the device it is controlling when the user presses it, and that the switch activates consistently. To test this, use a switch tester, (https://github.com/makersmakingchange/Simple-Switch-Tester) a continuity tester, or a working switch adapted device. Whichever option you use, the device should only be “on” when the switch is pressed, and it should consistently turn on when pressed.

There should not be noticeable stiffness or resistance when pressing the switch, and you may be able to hear a click when the tactile switch activates.

### Troubleshooting

The switch is always “On”.

This is often caused by a short circuit. Check to see if the wires from the mono cable are touching, or if solder is connecting the leads of the tactile switch together.

If the wires are touching, separate them and make sure they will not touch again by soldering, gluing, or removing excess wire. If the solder is touching, remove any excess solder.

The switch may also be sitting too high in the button base, so the button top is always pressing it. If that is the case, disassemble the switch and make sure the mounting lugs and second set of leads have been trimmed flush. Reassemble the switch, using a very small amount of glue to hold the tactile switch in place.

## MAKER GUIDE

© 2024 by Neil Squire. (https://neilsquire.ca/)

The switch is always “Off” or is inconsistent when pressed.

This is often caused by incomplete solder joints. Check the solder joints to ensure the solder has connected to both the wire and the leads of the switch. The wire should not slide on the lead if pulled gently.

This may also be cause by too much glue in the base, preventing the top from moving when it is pressed. Make sure the glue covering the mono cable in the base of the switch does not come above the edge of the recess in the base. If it does, remove the excess glue.

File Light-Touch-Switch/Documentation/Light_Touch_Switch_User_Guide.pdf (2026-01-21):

V1.0.0 | June 2024

## Light Touch Switch

## USER GUIDE


© 2024 Neil Squire. (https://neilsquire.ca/)
This work is licensed under the CC BY SA 4.0 License: http://creativecommons.org/licenses/by-sa/4.0 Files available at https://github.com/makersmakingchange/Light-Touch-Switch

## Overview

This document contains the necessary information to use the Light Touch Switch, a cost-effective 3D printable accessibility switch for people with physical disabilities.

## USER GUIDE

© 2024 Neil Squire. (https://neilsquire.ca/)

## Contents

Overview | 1
Introduction | 3
Features | 3
Specifications | 3
Compatibility | 3
Usage | 4
Takedown / Storage | 4
Cleaning | 4
Care | 4
Disposal | 4

## USER GUIDE


© 2024 Neil Squire. (https://neilsquire.ca/)

### Introduction

This device was originally created by Kevin Cross (https://www.thingiverse.com/davross/designs) as a DIY, low-cost assistive switch alternative to commercially available switches which would work with the Xbox Adaptive Controller (XAC). (https://www.xbox.com/en-CA/accessories/controllers/xbox-adaptive-controller) The Light Touch Switch is well-suited for use with one finger. It can be used with any switch controlled device that has a 3.55 mm mono cable jack.

The Light Touch Switch is a low-force switch for controlling electronic devices, such as phones / tablets, computers, adapted toys, and video games.

The Light Touch Switch is suitable for people with physical disabilities who may have limited strength and / or movement.

### Features

The Light Touch Switch uses a 3.5 mm mono cable to activate switch adapted device, and has a textured portion on the top to indicate where to press the switch for users with visual impairment. The mono cable end and textured portion of the cap are circled in the image below.

### Specifications

Item | Light Touch Switch
Size (Length x Width x Height) [mm] | 50 x 17 x 15
Mass [g] | 30
Operating force [grams of force] | 30-40
Activation distance [mm] | 0.7
Cable type | 3.5 mm mono cable

### Compatibility

The Light Touch Switch is compatible with any standard switch adapted device, such a switch adapted toys; switch interfaces for computers, smart phones, and tablets; and adapted gaming devices.

## USER GUIDE

© 2024 Neil Squire. (https://neilsquire.ca/)

### Usage

Plug the Light Touch Switch into the jack on a switch adapted device, and press the textured portion on the top of the switch to activate it. The switch will be “on” while it is pressed, and “off” when it is not. You may hear and feel a click when the tactile has been pressed.

Takedown / Storage
When not in use, the Light Touch Switch should be stored in a cool place out of direct sunlight. Extended exposure to sunlight will affect the plastic, and exposure to high temperatures will cause the plastic to warp.

### Cleaning

The 3D printed parts and cable of Light Touch Switch can be wiped with a damp cloth. Do not submerge the Light Touch Switch in water as this may destroy the electronics. Do not use hot water or clean in a dishwasher.

### Care

The Light Touch Switch is made of 3D printed plastic. Exposure to high heat may cause warping and/or negatively affect function. Extended exposure to sunlight will also weaken the plastic on the device.

The Light Touch Switch contains electronics and is not waterproof. If the device becomes wet, do not use it until it has completely dried.

### Disposal

PLA filament may be industrially compostable in your area. Check with your local waste management if PLA can be composted or must be thrown in the garbage.

Disassemble the Light Touch Switch and separate out the recyclable and compostable components, and those that must be thrown out. Electronics and batteries should be disposed of following your local waste management guidelines.

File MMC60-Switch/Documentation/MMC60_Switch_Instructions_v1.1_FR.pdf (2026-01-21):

# Commutateur MMC60

# GUIDE DE MONTAGE


02.

07.

03.

06.

04.

08.

PAGE 1 | CONCEPTION SIGNÉE MAKERS MAKING CHANGE

### FRONT

### BACK

Vérifiez qu’il n’y a pas de résidus de plastique dans le trou percé.

Pressez fermement le boulon à tête hexagonale afin de percer un trou.

Retirez le matériau de support.

05. Placez les pointes de l’écrou en T sur les fentes.

Serrez jusqu’à ce que l’écrou en T soit enfoncé le
plus possible. | Dévissez le boulon et retirez-le.
V1.1 | tiny.cc/MMC60

01.

# Commutateur MMC60

# GUIDE DE MONTAGE


12.

14.

16.

11.

13.

15.

10.
IMPORTANT: Pressez les broches imprimées en 3D contre la surface de travail afin de les enfoncer dans les quatre trous. Si les trous sont trop petits, utilisez un tournevis ou une pince coupante à affleurement pour les agrandir.
V1.1 | tiny.cc/MMC60 | PAGE 2 | CONCEPTION SIGNÉE MAKERS MAKING CHANGE

# 6 cm

Utilisez ceci
comme mesure:
0 | 1 cm | 2 cm | 3 cm
0.5cm | 0.5cm

Reliez les bornes A au moyen d’un fil, puis pliez-le en place. Reliez les bornes B au moyen d’un autre fil et pliez-le en place.

A
B

B

A

### 09. Assurez-vous que l’interrupteur de fin de course

est installé dans le bon sens.

# Commutateur MMC60

# GUIDE DE MONTAGE


18.

23.

17.

19.

22.

20.

24.

### FRONT

### BACK

21.

V1.1 | tiny.cc/MMC60 | PAGE 3 | CONCEPTION SIGNÉE MAKERS MAKING CHANGE

Aplatissez les fils contre le matériel de fixation en prenant soin de ne pas obstruer les deux trous.

Soudez les quatre carrés indiqués sur l’image. Ne pas souder les extrémités des bornes.

AUTOTEST: Branchez votre commutateur sur le gabarit de test au moyen d’un câble audio. Si votre commutateur est bien monté, le témoin DEL s’allumera.

1.

2.

3.

Servez-vous de l’encoche pour faciliter la mise en place de l’insertion.

# Commutateur MMC60

# GUIDE DE MONTAGE


25. 26.

27.

V1.1 | tiny.cc/MMC60 | PAGE 4

Insérez le couvercle du socle en orientant l’encoche
du trou de boulon vers le haut.

CONCEPTION SIGNÉE MAKERS MAKING CHANGE

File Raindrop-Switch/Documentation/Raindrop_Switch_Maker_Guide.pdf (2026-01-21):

V1.1 | June 2024

## Raindrop Switch

## MAKER GUIDE


© 2024 by Neil Squire. (https://neilsquire.ca/)
This work is licensed under the CC BY SA 4.0 License: http://creativecommons.org/licenses/by-sa/4.0
Files available at https://github.com/makersmakingchange/Raindrop-Switch | Page 1 of 16

### Overview

This document contains the necessary information to build the Raindrop Switch, a small affordable assistive switch.

## MAKER GUIDE

Files available at https://github.com/makersmakingchange/Raindrop-Switch | Page 2 of 16

### Contents

Overview | 1
Maker Checklist | 3
Maker To Do List | 3
Items to Give to User | 3
Tool List | 4
Tools / Equipment | 4
Supplies | 4
Personal Protective Equipment (PPE) | 4
Customization Guide | 5
3D Printing Guide | 5
3D Printing Summary | 5
3D Printing Settings | 5
Post-Processing | 5
Examples of Quality Prints | 6
Maker Component List | 7
Required Tools and Supplies | 7
Required Personal Protective Equipment (PPE) | 7
Raindrop Switch Assembly Steps | 8
Testing | 16
Troubleshooting | 16

## MAKER GUIDE

Files available at https://github.com/makersmakingchange/Raindrop-Switch | Page 3 of 16

### Maker Checklist

This list provides an overview of the steps required to build and deliver the Raindrop Switch

### Maker To Do List

Read through the Maker Guide to become familiar with required components, tools, supplies, safety gear, and overall assembly steps.
Talk to the User about customization options
- Switch base and cap can be printed in different colours
- How they would like to receive the “User Guide” (physical or soft copy) Order hardware components
Gather tools, supplies, and safety equipment.
Assemble the device
Test the Raindrop switch
Print “User Guide” (if the User would like a physical copy)

### Items to Give to User

Raindrop switch
“User Guide”

## MAKER GUIDE

Files available at https://github.com/makersmakingchange/Raindrop-Switch | Page 4 of 16

### Tool List

### Tools / Equipment

Tool ID | Description | Required / Recommended | Notes
T01 | Flush Cutters | Required | Trimming unused parts of the button
T02 | Soldering Iron | Required | Connecting the button and the cable
T03 | Hot Glue Gun | Required | Securing the switch components to the base
T04 | Pliers | Recommended | Straightening the leads to the button
T05 | Wire Strippers | Required | Cutting the cable, and stripping the component wires
T06 | Soldering Jig | Optional | Holds the button and cable in place for soldering

### Supplies

Supplies ID Description | Quantity | Notes
S01 | Solder | A small amount | Soldering the mono cable to the tactile switch.
S02 | Hot glue | A small amount | Holds the tactile switch in place and provides strain relief on the cable.

### Personal Protective Equipment (PPE)

PPE ID | Description | Notes
P01 | Safety Glasses | Protecting your eyes

## MAKER GUIDE

Files available at https://github.com/makersmakingchange/Raindrop-Switch | Page 5 of 16

### Customization Guide

The device can be printed in the user’s desired colour.

The base and cap can be printed in the same colour or printed in different colours.

### 3D Printing Guide

The device was originally printed on an Ender 3 using Cura.

Default slicer profile was used for all prints.

### 3D Printing Summary

Metrics | Single Unit
Total Print Time (min) | 56min
Total Number of Components | 3
Typical Total Mass (g) | 6g
Typical Number of Print Setups | 1

### 3D Printing Settings

Print File Name | Qty | Total Print Time (hr:min) | Mass (g) | Infill (%) | Support(Y/N) | Layer Height/ Nozzle Diameter(mm) | Notes
Raindrop_Base_v1.2.stl | 1 | 0:12 | 1 | 20 | N | 0.2/0.4
Raindrop_Cap_v1.0.stl | 1 | 0:08 | 1 | 20 | N | 0.2/0.4
Switch_Jig_12mm_v1.0.stl | 1 | 0:36 | 4 | 20 | N | 0.2/0.4

### Post-Processing

Inspect the 3D printed parts for any printing defects, sharp edges, or burrs. Sharp edges and burrs can be removed with sanding or deburring tools.

## MAKER GUIDE


Files available at https://github.com/makersmakingchange/Raindrop-Switch | Page 6 of 16

### Examples of Quality Prints

Compare your 3D prints to the images here. If there are significant differences, you may need to reprint the part.

Raindrop Switch
Raindrop_Base_v1.2.stl | Raindrop_Cap_v1.0.stl | Switch_Jig_12mm_v1.0.stl

## MAKER GUIDE


Files available at https://github.com/makersmakingchange/Raindrop-Switch | Page 7 of 16

### Maker Component List

Raindrop Switch
A01 Tactile
Button
QTY: 1 | A02 | Mono
Cable
QTY: 1 | A03 | Raindrop
Base

QTY: 1

A04 | Raindrop Cap

QTY: 1

Required Tools and Supplies
- Flush Cutters
- Soldering Iron
- Hot Glue Gun
- Pliers
- Wire Strippers
- Switch_Jig_12mm (optional)

Required Personal Protective Equipment (PPE)
- Safety Glasses

## MAKER GUIDE


Files available at https://github.com/makersmakingchange/Raindrop-Switch | Page 8 of 16

Raindrop Switch Assembly Steps

Step 01: Trim the button leads
Cut off the two leads flush on one side of the button (A01) using the flush cutters (T01).
Step 02: Bend the remaining leads
Take the two remaining leads on the button, and bend them 90 degrees using pliers (T04).

## MAKER GUIDE


Files available at https://github.com/makersmakingchange/Raindrop-Switch | Page 9 of 16
Step 03: Trim the mounting lugs
Cut off the two plastic mounting lugs completely flush using flush cutters (T01).
Step 04: Cut the mono cable in half
Using flush cutters (T01), cut the mono cable (A02) in half.

## MAKER GUIDE


Files available at https://github.com/makersmakingchange/Raindrop-Switch | Page 10 of 16
Step 05: Thread the cable onto the base
Thread the cut end of one half of the mono cable through the hole in the base of the switch (A03).
Step 06: Strip the end of the cable
Using wire strippers (T05), strip the last two centimeters of the mono cable. Twist the loose copper into a solid strand.

## MAKER GUIDE


Files available at https://github.com/makersmakingchange/Raindrop-Switch | Page 11 of 16
Step 07: Strip the interior cable
Strip the insulation off the remaining cable, and twist the loose wires into a solid strand.
Step 08: Wrap the wires around the switch leads
Hold the cable behind the switch and wrap the wire around the switch leads with a plier.

## MAKER GUIDE


Files available at https://github.com/makersmakingchange/Raindrop-Switch | Page 12 of 16
Step 09: Bend the wire
Hold the switch in place and cable the wire in between the two switch leads.
Step 10: Solder the cable to the button
Solder the cable to the leads on the switch using a soldering iron (T02). The soldering jig (T06) can be used to hold the assembly together while soldering. IMPORTANT: After soldering the two leads, test the switch by following the instructions in the testing section.

## MAKER GUIDE


Files available at https://github.com/makersmakingchange/Raindrop-Switch | Page 13 of 16
Step 11: Move the case closer to the switch
Pull the cable through the base so that the switch assembly is much closer to the base.
Step 12: Add hot glue to the base
Add a small drop of hot glue (T03) to the base. Do not add too much, a pin head sized blob is enough.

## MAKER GUIDE


Files available at https://github.com/makersmakingchange/Raindrop-Switch | Page 14 of 16
Step 13: Press the switch into the base
Press the switch into the recess in the base with the hot glue drop in it. Make sure the switch is sitting level in the case.
Step 14: Add hot glue onto the cap
Add a small drop of hot glue in the square recess in the cap. Do not add too much.

## MAKER GUIDE


Files available at https://github.com/makersmakingchange/Raindrop-Switch | Page 15 of 16
Step 15: Press the assembly onto the cap
Press the knob on the switch into the hot glue on the cap. To prevent hot glue in the cap from oozing downwards, press the case assembly onto the cap.
Step 16: Fill the hollow on the switch bottom
Fill the hollow on the bottom of the switch with hot glue to secure the cable. Do not overfill the hollow of the switch will not sit flat.

## MAKER GUIDE

Files available at https://github.com/makersmakingchange/Raindrop-Switch | Page 16 of 16

### Testing

Using a switch tester, test that the switch is working. The light should turn on when the switch is pressed, and turn off when the switch is released.

### Troubleshooting

If the switch is not working properly, check the solder joints between the button and cable to make sure the cable has not come loose from the cable.

If the lead on the button has broken off, replace it with a new button.

If the wire has broken off the cable, cut the cable back a centimeter and repeat steps 6-10 to reattach the cable.

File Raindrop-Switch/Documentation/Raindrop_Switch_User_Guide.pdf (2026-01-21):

V1.1 | June 2024

## Raindrop Switch

## USER GUIDE


© 2024 by Neil Squire. (https://neilsquire.ca/)
This work is licensed under the CC BY SA 4.0 License: http://creativecommons.org/licenses/by-sa/4.0
Files available at https://github.com/makersmakingchange/Raindrop-Switch | Page 1 of 4

### Overview

This document contains the necessary information to use the Raindrop Switch, a cost-effective accessible switch that is well-suited for use by a finger.

## USER GUIDE

Files available at https://github.com/makersmakingchange/Raindrop-Switch | Page 2 of 4

## Contents

Overview | 1
Introduction | 3
Features | 3
Specifications | 3
Compatibility | 3
Usage | 4
Initial Setup | 4
Regular Use | 4
Takedown / Storage | 4
Cleaning | 4
Care | 4
Disposal | 4

## USER GUIDE


Files available at https://github.com/makersmakingchange/Raindrop-Switch | Page 3 of 4

### Introduction

The Raindrop Switch is a cost-effective accessibility switch, an assistive device used by people with physical disabilities to control electronics (e.g. phones, computers, adapted toys, game controls, etc.).

This particular switch is well-suited for use by a finger. It can be plugged into any standard 3.5 mm AT interface and even the Xbox Adaptive Controller. Users can arrange multiple switches in an array to get input from more than one finger. The switch can be mounted using adhesive on the rear surface.

### Features

The Raindrop switch has two main components, the jack and the switch. The jack is the component that allows the Raindrop Switch to connect to the accessible device, and the switch is the component that allows the user to activate the connected device.

### Specifications

Item | <Device Name>
Size (Length x Width x Height) [mm] | 31x23x10
Mass [g] | 35
Number of jacks | 1

### Compatibility

The Raindrop Switch is compatible with all accessible devices that have a 3.5mm plug.

## USER GUIDE

Files available at https://github.com/makersmakingchange/Raindrop-Switch | Page 4 of 4

### Usage

Initial Setup
Take the jack on the switch, and plug in into the 3.5mm plug on the accessible device.

Regular Use
After plugging the switch into the accessible device, pressing the button will activate the plug that the switch is connected to.

Takedown / Storage
Holding the jack as close as possible to the accessible device, and gently pull on it to unplug it from the device. Loosely coil the wire and store it in a cool place out of direct sunlight.

### Cleaning

The Raindrop Switch can be wiped with a damp cloth.

### Care

The Raindrop Switch is made of 3D printed plastic. Exposure to high heat may cause warping and/or negatively affect function. Extended exposure to sunlight will also weaken the plastic on the device.

The Raindrop Switch contains electronics and is not waterproof. If the device becomes wet, make sure it is off and do not use it until it has completely dried. It may help to open any electronic enclosures to speed up drying and ensure it has completely dried.

### Disposal

PLA filament may be industrially compostable in your area. Check with your waste management company if PLA can be composted or must be thrown in the garbage.

Disassemble the Raindrop Switch and separate out the recyclable and compostable components, and those that must be thrown out. Electronics and batteries should be disposed of following your local waste management guidelines.

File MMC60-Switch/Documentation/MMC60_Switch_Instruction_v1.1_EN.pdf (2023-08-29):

# MMC60 Switch

# ASSEMBLY MANUAL


02.

07.

03.

06.

04.

08.

PAGE 1 | DESIGN BY MAKERS MAKING CHANGE

### FRONT

### BACK

Make sure there is no residual plastic in the punched hole. Push the hex bolt all the way to punch a hole.

Remove the support material.

05. Place the tee nut teeth on the slits.

Tighten until the tee nut is seated as far down as
possible. | Unscrew and remove bolt.
V1.1 | tiny.cc/MMC60

01.

# MMC60 Switch

# ASSEMBLY MANUAL


12.

14.

16.

11.

13.

15.

09. 10. Make sure to orient the limit switch correctly. IMPORTANT: Push the 3D printed pins against the table so it goes through the four holes. If the holes are too small, use a screwdriver or flush cutter to clear it.
V1.1 | tiny.cc/MMC60 | PAGE 2 | DESIGN BY MAKERS MAKING CHANGE

6cm

Use this to measure:

0 | 1cm | 2cm | 3cm
0.5cm | 0.5cm

Connect the A terminals together with one wire and bend in place. Connect the B terminals with the second wire and bend in place.

A
B

B

A

# MMC60 Switch

# ASSEMBLY MANUAL


18.

23.

17.

19.

22.

20.

24.

### FRONT

### BACK

21.

V1.1 | tiny.cc/MMC60 | PAGE 3 | DESIGN BY MAKERS MAKING CHANGE

Flatten the wires so it’s flush against the hardware mount. Avoid obstructing the two holes.

Solder the four indicated squares. Keep the tips of the terminals solder free.

TEST: Plug your switch into the testing jig using an audio cable. The LED will light up if your switch is built correctly.

1.

2.

3.

Use the keyed notch to guide the insertion.

# MMC60 Switch

# ASSEMBLY MANUAL


25. 26.

27.

V1.1 | tiny.cc/MMC60 | PAGE 4 | DESIGN BY MAKERS MAKING CHANGE

Insert the base top with the screw hole divot up .

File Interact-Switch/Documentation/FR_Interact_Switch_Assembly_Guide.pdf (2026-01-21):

V1.1 | AOÛT 2023

## Commutateur Interactif

## GUIDE DE MONTAGE

BOM 1. 1x socle de commutateur (imprimé en 3D) 2. 1x support de capuchon de bouton (imprimé en 3D) 3. 1x insertion de capuchon de bouton (imprimée en 3D) 4. 1x capuchon de bouton (imprimé en 3D) 5. interrupteur de fin de course Omron SS-3GP 6. 1x câble mono de 3,5 mm 7. 3x vis auto taraudeuses à tête cylindrique M2.5x12 ou no 4, 3/8 po

© 2023 by Neil Squire / Makers Making Change. Le présent ouvrage est placé sous licence CC BY SA 4.0 : http://creativecommons.org/licenses/by-sa/4.0
Les fichiers sont accessibles sur : https://github.com/mwturvey/InteractSwitch (en anglais seulement) | Page 1 of 6

### Required Components

### Outils Requis

- Fer à souder et soudure
- Pince à dénuder
- Tournevis

### Équipement de protection individuelle (ÉPI) requis

- Lunettes de sécurité

### Attribution

La conception du commutateur Interactif de Mike Turvey est utilisée sous licence CC-BY 4.0. Ces instructions ont été adaptées des instructions originales de montage du commutateur Interactif par Mike Turvey, utilisées sous licence CC-BY 4.0. (en anglais seulement)

## GUIDE DE MONTAGE

© 2023 by Neil Squire / Makers Making Change.


Le présent ouvrage est placé sous licence CC BY SA 4.0 : http://creativecommons.org/licenses/by-sa/4.0
Les fichiers sont accessibles sur : https://github.com/mwturvey/InteractSwitch (en anglais seulement) | Page 2 of 6

### GUIDE DE MONTAGE

### Étape 1 - Préparer le câble

Coupez et jetez l’une des fiches du câble audio mono.
Utilisez la pince à dénuder pour retirer soigneusement environ 15 mm de l’isolant extérieur de l’extrémité.

### Étape 2 — Préparer les fils du câble

Enroulez les brins de cuivre pour former un seul fil.

Utilisez la pince à dénuder pour retirer environ 5 mm d’isolant de l’autre fil.

(Remarque : Votre câble peut être différent. Dans le cas où deux fils sont isolés, retirez 5 mm de l’extrémité de chaque fil).

## GUIDE DE MONTAGE

© 2023 by Neil Squire / Makers Making Change.


Le présent ouvrage est placé sous licence CC BY SA 4.0 : http://creativecommons.org/licenses/by-sa/4.0
Les fichiers sont accessibles sur : https://github.com/mwturvey/InteractSwitch (en anglais seulement) | Page 3 of 6

### Étape 3 — Enfiler le câble dans le socle du commutateur

Faites passer le câble dans le trou du socle du
commutateur. Vous ne pourrez pas le faire
après avoir soudé les fils sur l’interrupteur de
fin de course.

### Étape 4 — Souder les fils à l’interrupteur de fin de course

Soudez les fils à l’interrupteur comme illustré
ci-contre.

Remarque : Soudez les deux fils les plus proches du bouton de l’interrupteur.

Autotest : branchez votre interrupteur de fin de cours sur un dispositif activé par commutation puis appuyez sur son bouton.

## GUIDE DE MONTAGE

© 2023 by Neil Squire / Makers Making Change.


Le présent ouvrage est placé sous licence CC BY SA 4.0 : http://creativecommons.org/licenses/by-sa/4.0
Les fichiers sont accessibles sur : https://github.com/mwturvey/InteractSwitch (en anglais seulement) | Page 4 of 6

### Étape 5 — Installer l’interrupteur de fin de course dans le socle

Placez l’interrupteur dans le socle du
commutateur comme illustré ci-contre.

Installez l’interrupteur de sorte que lorsque le câble vient vers vous, son bouton est décalé vers la gauche. Veillez à ce qu’aucun fil ne soit coincé en dessous, empêchant ainsi la sortie complète de l’interrupteur de fin de course.

Enfoncez ensuite le câble dans la fente, comme illustré ci-contre.

### Étape 6 — Assembler le capuchon du bouton

Retournez le capuchon du bouton et introduisez-y son insertion. Si vous n’êtes
pas sûr de la taille à utiliser, commencez
par une insertion de 0,5 mm.

## GUIDE DE MONTAGE

© 2023 by Neil Squire / Makers Making Change.


Le présent ouvrage est placé sous licence CC BY SA 4.0 : http://creativecommons.org/licenses/by-sa/4.0
Les fichiers sont accessibles sur : https://github.com/mwturvey/InteractSwitch (en anglais seulement) | Page 5 of 6

### Étape 7 — Terminer l’assemblage du capuchon de bouton

Insérez le support de capuchon de bouton
dans le capuchon de bouton assemblé.
L’orientation de la partie « ouverte » n’a
pas d’importance.

Remarque : pour une meilleure fluidité du commutateur, poncez les bords du support de capuchon de bouton à l’endroit où il frotte sur celui-ci.

### Étape 8 — Assembler le commutateur

Alignez les trois montants du support de capuchon du commutateur sur les trois trous du socle du commutateur. Fixez le support de capuchon du commutateur au socle du commutateur à l’aide de trois vis.

Remarque : Veillez à ne pas trop serrer les vis. Serrez-les jusqu’à ce que vous remarquiez que la résistance augmente et que le support de capuchon du commutateur est fermement appuyé contre le socle du commutateur.

## GUIDE DE MONTAGE

© 2023 by Neil Squire / Makers Making Change.


Le présent ouvrage est placé sous licence CC BY SA 4.0 : http://creativecommons.org/licenses/by-sa/4.0
Les fichiers sont accessibles sur : https://github.com/mwturvey/InteractSwitch (en anglais seulement) | Page 6 of 6

### Autotest

En dernier lieu, il convient de tester votre commutateur. S’il s’agit de votre premier commutateur, vous aurez probablement besoin de le tester et de déterminer la taille appropriée de l’insertion de capuchon du commutateur.
Lorsque je teste un commutateur, je commence par appuyer plusieurs fois dessus. Tapez-le partout, à plusieurs reprises. Chaque fois que vous appuyez dessus, vous devez entendre un clic lorsqu’il s’enfonce, puis un clic lorsqu’il remonte. Il ne doit jamais rester coincé. Si vous agitez son capuchon, il doit bouger un tant soit peu, sans toutefois donner l’impression de s’entrechoquer. Branchez ensuite le commutateur sur un dispositif activé par commutation pour vous assurer qu’il fonctionne.

### Dépannage

Problème | Solution
Le capuchon du commutateur n’est pas assez serré et s’entrechoque facilement. | Utilisez une insertion de capuchon du commutateur plus grande/épaisse
Le commutateur n’émet aucun bruit lorsqu’il est enfoncé. | Utilisez une insertion de capuchon du commutateur plus petite/plus mince. Une insertion trop grande peut faire en sorte que l’interrupteur de fin de course reste toujours enfoncé. Lorsque c’est le cas, il est fréquent que l’interrupteur de fin de course émette un « clic » en position fermée, lorsque vous vissez le tout ensemble, mais jamais en position ouverte.
Le commutateur reste coincé/ne remonte pas toujours. | Utilisez une insertion de capuchon du commutateur plus petite/plus mince. Une taille plus mince peut suffire à résoudre ce problème.
Le commutateur émet un clic, mais le dispositif activé par commutation ne se met pas en marche. | Branchez le dispositif activé par commutation dans un interrupteur en bon état de marche, simplement pour vous assurer qu’il fonctionne correctement. Vérifiez que la fiche est bien branchée dans le dispositif. Il est possible que la soudure soit endommagée et qu’il faille la refaire. Il se peut que le fil soit rompu à l’intérieur et qu’il faille le remplacer. C’est un point de défaillance particulièrement courant sur les anciens commutateurs.

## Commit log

2026-01-21 Updated all switch files in the kit
    - Updated all files for the switches contained in this kit
    - Organized switch folders to follow same format as other repos (folder structure with Build_Files, etc.)
    [ButtonBase.SLDPRT, ButtonBase_Spade.SLDPRT, ButtonBase_Spade.STL, ButtonCapHolder.SLDPRT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]
2026-02-04 Added documentation for MMC60
    - Added BOM and Word docs for MMC60 documentation
    [MMC60_Assistive_Switch_BOM.csv, MMC60_Assistive_Switch_BOM.xlsx]
2026-02-04 Added automation for copying devices to a kit
    - Added the file to copy device files to the kit repo
    - Removed old version I was trialing before
2026-02-13 Updating STL files
    - Updated STL files to match the most up-to-date base
    - Flexure and base top have two indents for finding feature on base bottom
    - Jack mount has three screw holes
    - Pin matches jack mount
    [RFS_Base_Top.stl, RFS_Flexure.stl, RFS_Pins.stl, RFS_Sw_Jack_Mount.stl]
